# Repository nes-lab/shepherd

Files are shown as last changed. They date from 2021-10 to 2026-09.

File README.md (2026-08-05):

# SHEpHERD: SyncHronized Energy Harvesting Emulator RecorDer








**Testbed-Website**: <https://nes-lab.github.io/shepherd-nova>

**Python-Tools for Users**: <https://github.com/nes-lab/shepherd-tools>

**Documentation**: <https://nes-lab.github.io/shepherd>

**Main Project**: <https://github.com/nes-lab/shepherd>

**Targets-HW & -SW**: <https://github.com/nes-lab/shepherd-targets>

**WebAPI-Repo**: <https://github.com/nes-lab/shepherd-webapi>

**Dev-Documentation**: <https://github.com/orgua/shepherd-v2-planning>

---

Batteryless sensor nodes depend on harvesting energy from their environment.
Developing solutions involving groups of batteryless nodes requires a tool to analyze, understand and replicate spatio-temporal harvesting conditions.
*shepherd* is a testbed for the batteryless Internet of Things, allowing to record harvesting conditions at multiple points in space over time.
The recorded data can be replayed to attached wireless sensor nodes, examining their behavior under the constraints of spatio-temporal energy availability.

**Features**

 - High-speed, high resolution current and voltage sensing
 - Technology-agnostic: Currently, solar and kinetic energy harvesting are supported
 - Remote programming/debugging of ARM Cortex-M MCUs using Serial-Wire-Debug
 - High resolution, synchronized GPIO tracing
 - Configurable, constant voltage power supply for attached sensor nodes
 - Level-translated serial connection to the attached sensor nodes

For a detailed description see our [Paper](https://wwwpub.zih.tu-dresden.de/~mzimmerl/pubs/geissdoerfer19shepherd.pdf) or the [official documentation](https://nes-lab.github.io/shepherd/).

A *shepherd* instance consists of a group of spatially distributed *shepherd* nodes that are time-synchronized with each other.
Each *shepherd* node consists of a [BeagleBone](https://beagleboard.org/bone), the *shepherd* cape and either an energy harvesting source or a target MCU board to test.

This repository contains the hardware design files for the shepherd cape, the software running on each *shepherd* node as well as the tool to orchestrate a group of *shepherd* nodes connected to a network.

## Quickstart

Start by assembling your *shepherd* nodes, consisting of a BeagleBone Green/Black, a *shepherd* cape, a harvesting capelet and a target capelet.
The next step is to manually install the latest Ubuntu Linux on each BeagleBone.
You can install it to SD-card or the on-board eMMC flash, following [the official instructions](https://elinux.org/BeagleBoardUbuntu).
Make sure to follow the instructions for **BeagleBone**. Alternatively there are two more detailed guides in the [shepherd documentation](https://nes-lab.github.io/shepherd/user/getting_started.html).

The following instructions describe how to install the *shepherd* software on a group of *shepherd* nodes connected to an Ethernet network.
We assume that your local machine is connected to the same network, that the nodes have internet access and that you know the IP address of each node.

If you haven't done it yet, clone this repository to your local machine:

```shell
git clone https://github.com/nes-lab/shepherd.git
```

Next, install the tools used for installing and controlling the *shepherd* nodes.
We'll use [Ansible](https://www.ansible.com/) to remotely roll out the basic configuration to each *shepherd* node and *shepherd-herd* to orchestrate recording/emulation across all nodes.
The tools are hosted on `PyPI` and require Python version >= 3.6.
You'll also need to have `sshpass` installed on your machine, which is available through the package management system of all major distributions.
Install the tools using `pip`:

```shell
pip3 install ansible shepherd-herd
```

The `inventory/herd.yaml` file shows an example of how to provide the host names and known IP addresses of your BeagleBones.
Adjust it to reflect your setup.
You can arbitrarily choose and assign the hostnames (sheep0, sheep1, in this example) and the ansible_user (jane in this example).
[**TODO:** update description with roles].

```yaml
sheep:
  hosts:
    sheep0:
        ansible_host: 192.168.1.100
    sheep1:
        ansible_host: 192.168.1.101
    sheep2:
        ansible_host: 192.168.1.102
  vars:
    ansible_user: jane
```

Now run the `bootstrap.yml` *Ansible* playbook, which sets the hostname, creates a user and enables passwordless ssh and sudo:

```shell
ansible-playbook deploy/bootstrap.yml
```

Finally, use the `deploy.yml` playbook to set up the *shepherd* software with the configured roles from inventory:

```shell
ansible-playbook deploy/deploy.yml
```

## Usage

Record two minutes of data:

```shell
shepherd-herd harvester -d 120 -o recording.h5 -a mppt_voc
```
The command starts the recording asynchronously and returns after all nodes have started recording.
While the nodes are still recording (indicated by blinking of LED 1 and 2), prepare a directory on your local machine:

```shell
mkdir ~/shepherd_recordings
```

After the nodes stop blinking, you can retrieve the data to analyze it on your local machine:

```shell
shepherd-herd retrieve recording.h5 ~/shepherd_recordings
```

For a detailed description of the [HDF5](https://en.wikipedia.org/wiki/Hierarchical_Data_Format) based data format, refer to the [corresponding documentation](https://shepherd-testbed.readthedocs.io/en/latest/user/data_format.html).

Finally, replay the previously recorded data to the attached sensor nodes, recording their power consumption:

```shell
shepherd-herd emulator -o consumption.h5 recording.h5
```

Try `shepherd-herd --help` or check out the documentation [here](https://shepherd-testbed.readthedocs.io/en/latest/user/cli.html#shepherd-herd) for a list of all options.

## Problems and Questions

If you experience issues or require additional features, please get in touch via e-mail or by creating an issue on GitHub. The issue-tab also gives an overview for current roadmaps and milestones.

## People

*shepherd* development is lead at the Networked Embedded Systems Lab at TU Dresden & TU Darmstadt as part of the DFG-funded project Next-IoT.

The following people have contributed to *shepherd*:

 - [Kai Geissdoerfer](https://www.researchgate.net/profile/Kai_Geissdoerfer)
 - [Mikolaj Chwalisz](https://www.tkn.tu-berlin.de/team/chwalisz/)
 - [Marco Zimmerling](https://wwwpub.zih.tu-dresden.de/~mzimmerl/)
 - [Justus Paulick](https://github.com/kugelbit)
 - [Boris Blokland](https://github.com/borro0)
 - [Jonas Kubicki](https://github.com/jonkub)
 - [Ingmar Splitt](https://github.com/nes-lab)

## Release-Procedure

Once you have a clean, stable and tested version, you should bump the version number to current year, month and release-number (YYYY.MM.r).

- increase version number by executing ``bump2version`` (see cmds below)
- update changelog in ``CHANGELOG.md``
- run unittests locally
  - sheep-package on observers
  - herd-tool on host
  - pru-python-module (in `software/firmware/pru0-module-py`)
  - fresh installation on Linux image via ansible
  - additionally every push gets automatically tested by GitHub workflows
- install and run ``prek`` for QA-Checks (pre-commit plugin-replacement), see steps below
- move code from dev-branch to main by PR
- add tag to commit - reflecting current version number - i.e. ``v25.5.1``
  - GitHub automatically creates a release & pushes the release to PyPI
- update release-text with latest Changelog (from `CHANGELOG.md`)
- rebase dev-branch

```Shell
prek run --all-files

# additional QA-Tests (currently with open issues)
ty check

bump2version --allow-dirty --new-version 2026.08.1 patch
# version-format: YYYY.MM.r
```

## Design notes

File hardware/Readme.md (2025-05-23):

# Shepherd specific Hardware

## Overview

Hardware-Subdirectories contain the necessary design-files to manufacture a shepherd observer node.

- `_deprecated`: design files for hardware that still floats around in the lab
- `cape_v#.#`: most recent version of shepherd cape for the BBone
- `case_lasercut`: deployment version for testbed
- ~~`power_in`:~~ low noise voltage regulator with < 17 V Input for TP-Link POE-Adapters that fail to produce 5V on newer Cisco Switches
- Targets are in dedicated [targets-repo](https://github.com/nes-lab/shepherd-targets/tree/main/hardware)

## Photos

### Cape v2.4

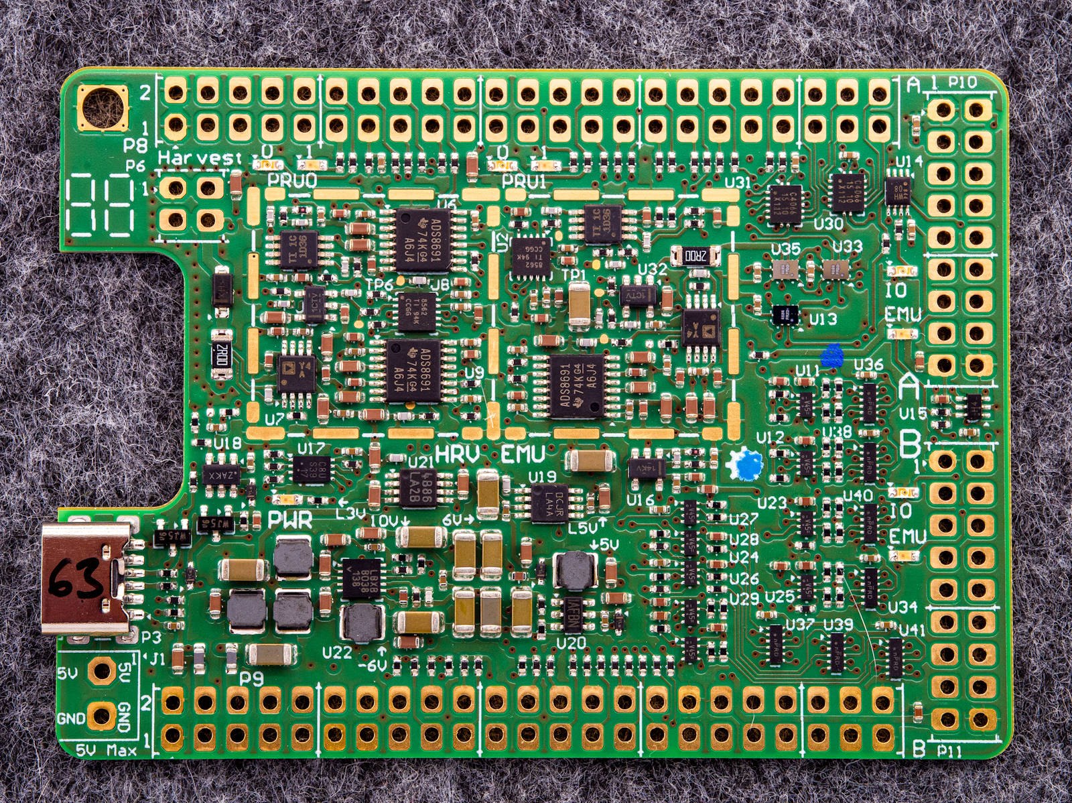
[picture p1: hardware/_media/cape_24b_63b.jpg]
Cape24b


More pictures are stored for QA in [planning-repo](https://github.com/orgua/shepherd-v2-planning/tree/main/doc_testbed/photos_PCBs).

### Cape v2.5

No pictures available yet. Hardware is currently tested and then deployed.

### Observers

Assembled in October 2024 for the deployment at TU Dresden. These nodes contain:

- TP-Link POE Splitter
- BeagleBone Green
- Shepherd Cape v2.4
- [nRF FRAM Target v1.3](https://github.com/nes-lab/shepherd-targets/tree/main/hardware/shepherd_nRF_FRAM_Target_v1.3e)
- Power-in-PCB
- Laser-cut case

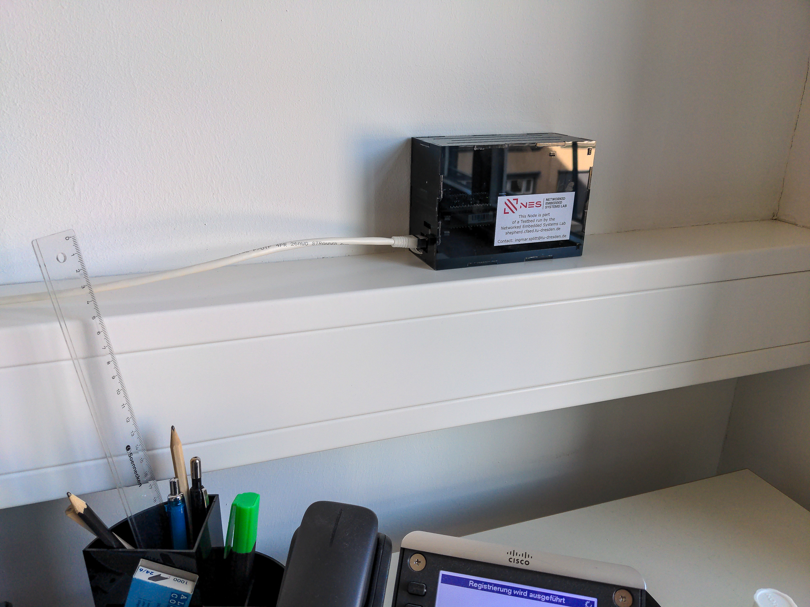
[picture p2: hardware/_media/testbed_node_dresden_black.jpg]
target_black


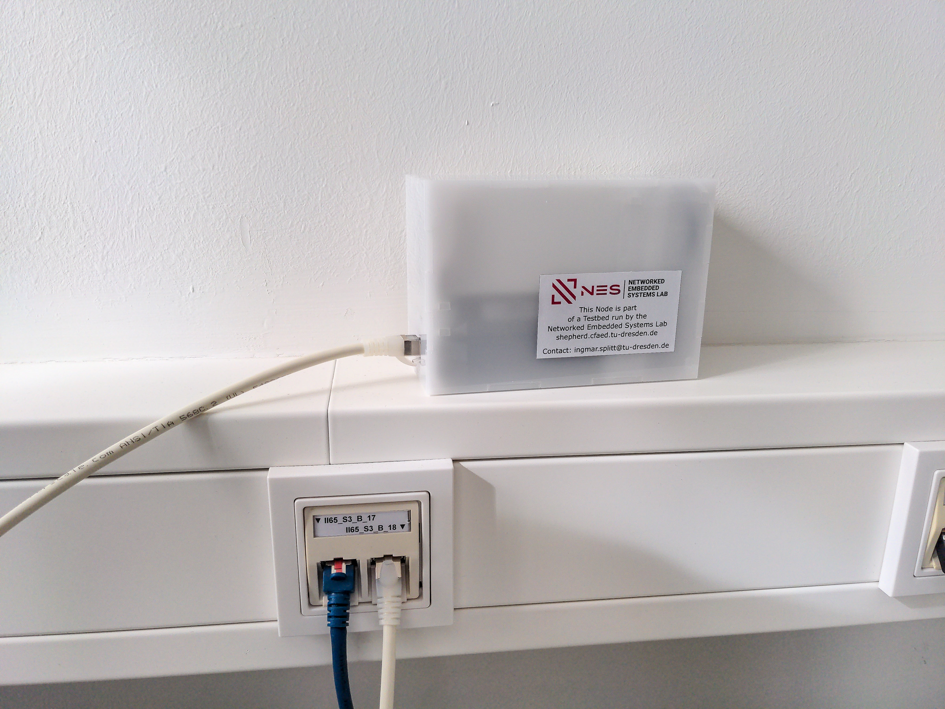
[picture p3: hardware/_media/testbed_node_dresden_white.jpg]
target_white


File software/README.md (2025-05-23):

# Software for Shepherd-Testbed

A collection of components and subprojects needed for the testbed. Bold items are needed for a local shepherd instance.

- **`firmware`**: time-critical gpio-sampling and emulation of virtual power source in PRUs of BeagleBone
- `gps-overlay`: kernel-module to allow syncing time via GPS
- **`kernel-module`**: low level system interface in between sheep-software (python) and PRUs
- `openocd`: (semi-deprecated) configuration for programming targets via openOCD
- `pps-gmtimer`: kernel-module to sync to a pps-time-signal
- **`python-package`**: sheep-software running on the beaglebone
- `shepherd-calibration`: python-software to calibrate the cape using a Keithley Sourcemeter
- `shepherd-tools`: sub-git for python user-module to handle measurements and access the data
- `shepherd-devicetest`: python-software to test & validate all parts of a cape
- **`shepherd-herd`**: python-software to control sheep / observers
- `shepherd-targets`: sub-git for target hardware and default firmwares
- `shepherd-webapi`: sub-git for the API and Website of the official testbed instance
- `debug_analyze_time_sync`: python-software for measuring sync between observers on gpio-level
- `debug_compare_vsources`: python-scripts to run virtual power source on PRU, shared-lib & python-port

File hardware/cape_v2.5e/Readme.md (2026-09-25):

## Main Goals

- replace old target connector by new edge connector
- redo interface to target completely
- add 17 V regulator to clean up POE-Supply
- add more GPIO (remove harvester as a tradeoff)

## Changes

### Implemented Changes v2.5a

- lower current-limiting resistors from 470 R to 240 R (see new target)
- emu U32 replace OPA189 by OPA388
- LP for InAmp AD8421 ⇾ 80kHz with 2x 100R, +2x 1nF to GND
- change invNr-Sys to solid white rect
- Emu - use 10mV Ref directly, without Switch
- Rec - use GND as Ref directly
- stabilize 10 mV ⇾ 1uF increase to 2x 10uF, 2R increase to 10R
- replace electrolytic Caps by MLCC (Optionals on Backside)

### Implemented Changes v2.5b/c

- production optimized for JLC
  - 6 layer includes via filling & capping (type 7) -> optional as via in pad is not used
  - vias were reduced to 0.2 mm hole, 0.35 ring dia
- replace target header with 40pin edge-Connector
- add 17V converter (previously external)
- Screw-Connector now supports 7 - 17V
- remove XYZ - for this last version - testbed only
  - usb-input
  - harvester frontend
  - ~~external switch & LED~~
- pin-changes on BBB Sockets, documented in `shepherd-git/hardware/_deprecated/beaglebone_pinout_concept.xlsx`
  - P8_14 is GPIO7, was targets GPIO0
  - P8_17 is GPIO8, was targets GPIO1
  - P8_27 is pru1_GPIO8, was pru_uart_tx
  - P8_28 is pru1_GPIO10, in addition to PRU1-LED0 (switch to input)
  - P8_29 is pru1_GPIO9, was pru1_batOK (switch to input)
  - P8_30 is pru1_GPIO11, in addition to PRU1-LED1 (switch to input)
  - P8_37 is now controlling direction of gpio-group A
  - P8_38 is now controlling direction of gpio-group B
  - P8_40 is pru1_GPIO7, was pru_uart_rx
  - P9_14 is now controlling direction of gpio-group C, was EN_Recorder
  - P9_25 is free, was CS_ADC2_REC
  - P9_27 is PWR_GOOD_L, was CS_DAC_REC
  - P9_41B is PWR_GOOD_H, was CS_ADC1_REC
- Target mapping Changed!
  - Target-GPIO9..11 are now input pru0-r31 (P8_29, P8_28, P8_30)
  - Target_GPIO0 is now UART-RX
  - BBone Pins changed
  - PinDirections are different
  - new BBone to target mapping is in separate section below, it now supports recording 12 pins
- GPS-Sync-Header added

### Implemented Changes v2.5d

- BOM-Trouble
  - NLAS4684 / NLAS4684FCT1G not available at all
    - Analog Switch, Dual SPDT, 500 mOhm Rds, 300 mA continuous, 500 mA peak, <10 nA Leakage (1 nA for -55 to 25°C)
    - we still have **~200x NLAS4684MN**, so will switch to that for now (+ larger, safer package)
  - PI5A4158 / PI5A4158ZAEX currently not avail
    - Analog Switch, Dual SPDT, 800 mOhm Rds, ~40 nA Leakage, high speed ~150 MHz with < 40 pF
    - PI3USB102G: 4 Ohm, 5V5 max, 6 pF, **BUT** 200 nA leakage
    - PI5A23157: 10 Ohm, 6V max, 18 pF, **BUT** 50 - 1000 nA leakage
    - **PI5A4157 / 729-PI5A4157CEX: single channel version of same IC, but only larger SC70 package (2.2x2.4) available**
    - **729-PI5A4157ZUEX**: UDFN-Package, 1x1 mm, mouser totally hides out of life parts, is in stock
  - LP2989-3.3 not avail as VSSOP-8 / TSOP
    - switch to WSON?
    - **926-LP2989AIMM33NOPB**, same but double the price
  - 10k 0402 667-ERJ-2GEJ103X -> 603-RC0402FR-7W10KL
  - 5.1k 0402 667-ERJ-2RKF5101X -> 603-RC0402FR-075K1L

## Implemented Changes v2.5e

- 1uF 10V is both used in 0402 & 0603
- holes on panel can be 3.2 mm for stencil printer
- QR Code can now be directly created in Altium
- larger tag-field (upper left corner)
- perforated breaking lines on panels  (extension of milled line)
- cage with paste?
- JST-Connector needs paste on mech-pad
- panel-bridge under JST - bad coincidence
- screw-hole could have vias around (safer, if inner metal scrapes off) -> it already has
- show label on 10mV
- add testpoints for voltages, avoid touching components
- Label reads "v2.5c" not 2.5d
- pin 1 marking bigger on most ICs
- **uart-sys pins are swapped, R66 & R68 need to be crossed manually**

## Errata & future Improvements

- ~~[modularize cape by function (Pwr, hrv, emu, gpio)](https://github.com/orgua/shepherd-v2-planning/blob/main/docs/10_capes/cape_v30_design.md)~~
  - reduce complexity
  - make iterations easier
  - reduce cost (cape is either hrv or emu)
  - trivial switching of platforms
- allow routing AUX-voltage (second output of DAC) to the same target port to mimic V_Sense to allow developing better intermittent algorithms (allows sensing emulated V_harvest or V_storage_cap)
  - two GPIO available for the analog switch (48, 117) - can be slow sysgpio
  - current 40 Pin target-connector has two NC pins left
- [route reset-line to target](https://github.com/nes-lab/shepherd/issues/164)
  - current 40 Pin target-connector has two NC pins left
- ~~support 4 Target Ports?~~
- Target-Connector is more useful right-angled, there are two versions:
  - `-RA`: SMD, right angle, Double the price
  - `-EM2`: Edge-mount, needs paste on both sides, even pricier than `-RA`
  - maybe it is cheaper to just plug in an interface PCB with a second connector to get the same result
- edge-PCB Target-Connector replace with FPC- or FCC-cable (flex-printed-circuit, flex-circuit-connector) to be less constraint positioning the target
  - features to keep: rotation-safe & shielded (currently 12x extra GND)
  - needed IO: 16 GPIO, 2 Voltages, 2 PwrGood, 4 Prog, 1+ GND => 25+ Pins
    - +1x for aux voltage
    - +1x for reset line (nRF & msp have nReset) -> 2 lines or negate if needed
    - +2x-3x for I2C-EEPROM (Write-Protection)
    - in total 5 pins extra
  - 40 pin FFC/FPC, 0.5 mm Pitch, 1.5€ -> 05-40-A-0050-A-4-06-4-T-HF
  - 40 pin connector has similar space req. as edge connector, 0.5 € per connector, FFC2B35-40-G
- NOTE: PI5 is the hardest part to place & source (but has to be replaced anyway)
  - main point of failure during production & hard to fix
- header to interface SBC as SMD? the goal is to speed up assembly with more automation
  - this would also make it worthwhile to p'n'p the bottom side (7 Caps)
- P2 Connector for external triggering & signaling has no real use-case
- describe P3 on PCB -> sync-port
- add shutdown-button (is missing on newer green eco)
- 5V input is enough - either add second input or remove 17V Reg (prone to burning out)

## Target Pin Def

### Target Port - Cape 2.4 (previous one)

```
pru_reg     name            BB_pin	sys_pin sys_reg
r31_00      TARGET_GPIO0    P8_45	P8_14, g0[26] -> 26
r31_01      TARGET_GPIO1    P8_46	P8_17, g0[27] -> 27
r31_02      TARGET_GPIO2    P8_43	P8_16, g1[14] -> 46
r31_03      TARGET_GPIO3    P8_44	P8_15, g1[15] -> 47
r31_04      TARGET_GPIO4    P8_41	P8_26, g1[29] -> 61
r31_05      TARGET_GPIO5    P8_42	P8_36, g2[16] -> 80
r31_06      TARGET_GPIO6    P8_39	P8_34, g2[17] -> 81
r31_07      TARGET_UART_RX  P8_40	P9_26, g0[14] -> 14
r31_08      TARGET_UART_TX  P8_27	P9_24, g0[15] -> 15
r30_09/out  TARGET_BAT_OK   P8_29	-
```

### Target Port - Cape 2.5d (this revision)

```
pru_reg       name              BB_pin	sys_pin sys_reg
pru1_r31_00   TARGET_GPIO0/uRx  P8_45	P9_26, g0[14] -> 14 (also Sys/PRU-UART) SYS_PINs have swapped UART
pru1_r31_01   TARGET_GPIO1/uTx  P8_46	P9_24, g0[15] -> 15 (also Sys/PRU-UART) SYS_PINs have swapped UART
pru1_r31_02   TARGET_GPIO2      P8_43	P8_16, g1[14] -> 46
pru1_r31_03   TARGET_GPIO3      P8_44	P8_15, g1[15] -> 47
pru1_r31_04   TARGET_GPIO4      P8_41	P8_26, g1[29] -> 61
pru1_r31_05   TARGET_GPIO5      P8_42	P8_36, g2[16] -> 80
pru1_r31_06   TARGET_GPIO6      P8_39	P8_34, g2[17] -> 81
pru1_r31_07   TARGET_GPIO7      P8_40	P8_14, g0[26] -> 26
pru1_r31_08   TARGET_GPIO8      P8_27	P8_17, g0[27] -> 27
pru1_r31_09   TARGET_GPIO9      P8_29	-
pru1_r31_10   TARGET_GPIO10     P8_28   - !! PRU1-LED0, direction must be changed in DTree for debugging
pru1_r31_11   TARGET_GPIO11     P8_30   - !! PRU1-LED1, direction must be changed in DTree

pru0_r30_05   PWR_GOOD_L        P9_27     (was CS_DAC_REC), gets added to bit 12 for GPIO-Sampling
pru0_r30_06   PWR_GOOD_H        P9_41B    (was CS_ADC1_REC), gets added to bit 13 for GPIO-Sampling
pru0_r30_07   - (free)          P9_25     (was CS_ADC2_REC)
```

## Commissioning Steps & Tests

### Manual Soldering

- 2Pin Screw-Header ⇾ VoltageInput
- 2x 2x46 Pinheader ⇾ BBone Port
- 5x 220 uF 6V3 MLCC on backside
- 2x 47 uF 16V MLCC 0on backside

### Initial Test

- visual
  - all ICs and diodes correct orientation
  - no visible shorts or other defects
  - R13 is DNP (at left edge, middle, next to coil)
- 7V In:
  - 15-17 mA, with 18x PI5 180deg flipped
  - 14-15 mA with PI5 removed or correctly oriented
  - first converter (U5/TPS62913) and its coil warms up by 7 K above ambient
- EN-Pin: 52-55 mA, OK, Converter +10K
  - 5V In directly after 17V stage (with TPS removed) 1 mA off vs 50 mA when on
  - warmest part is U3 - AD8421 InAmp (+5K from Ambient)
  - Power-Hotspots: U22, U19, U21,
  - Emu-Hotspots: U4, U3, U1,
  - GPIO-Hotspots: U7 (only one of many?)
- Voltages
    - L5V ⇾ 5.000 V
    - L3V3 ⇾ 3.295 V
    - 6V ⇾ 6.19 V
    - 10V ⇾ 9.71 V
    - -6V ⇾ -5.99 V
    - 10mV ⇾ 0.010 V
    - 5V ⇾ 5.20 V

### Verification and Log

Logs are stored in [Planning-Repo](https://github.com/orgua/shepherd-v2-planning/blob/main/doc_testbed/Cape25e_pre-deployment-tests.xlsx)

run test-firmware with real harvest (will be intermittent)

```Shell
sudo shepherd-sheep -v run ./python-package/example_config_emulation.yaml
```

run test-firmware with direct-vsrc and 3000mV recording

```Shell
sudo shepherd-sheep -v run /etc/shepherd/example_config_emulation.yaml
ll /var/shepherd/recordings/
scp jane@sheep0://var/shepherd/recordings/emu_2026-02-* ./
# -> run also on second port
```

Plot both

```Shell
shepherd-data plot .\ -e10
shepherd-data plot .\ -e"0.2"
```

Extract GPIO

```Shell
shepherd-data extract-gpio .\
# ! GPIO9to11 show no movement, these are allwaysRX, same as GPIO8 -> old device-tree
```

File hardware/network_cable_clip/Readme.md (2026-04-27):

# 3D-Printed Cable Clip

## Features

- holds cable with up to 6.5 mm diameter cable
- can take 1 to 4 magnets (4 mm diameter, 2 mm height)
- magnets can be pushed inside from the side of the cable-channel
- < 1 g PLA filament
- can be printed without support

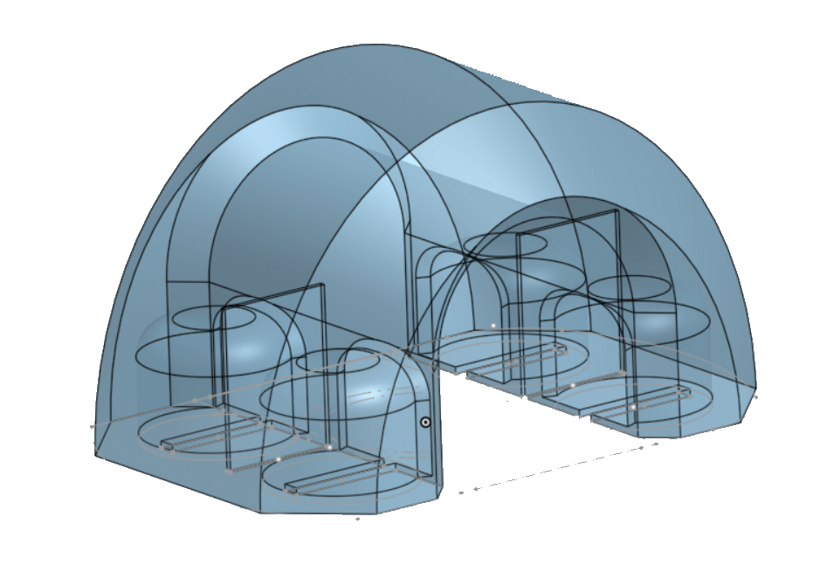
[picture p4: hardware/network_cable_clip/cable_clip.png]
rendered


[Designed in onshape](https://cad.onshape.com/documents/66bf84de817494616f210bb4/w/bc75bb6701e47c344748dd48/e/8d123086b6a33f87c60c09e2)

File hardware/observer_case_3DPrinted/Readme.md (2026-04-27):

# 3D Printed Case for the Observer Nodes

## Features

- high airflow case for Beaglebone, Cape & POE-Adapter
- internal rails for the PCBs
- feet with space for cylindrical magnets (8x3 mm, Dxh) for over head installation
- two parts that clip together
- openings for all emulator related ports
- 36 g PLA filament
- can be printed without support (flip end-face to print-plate)

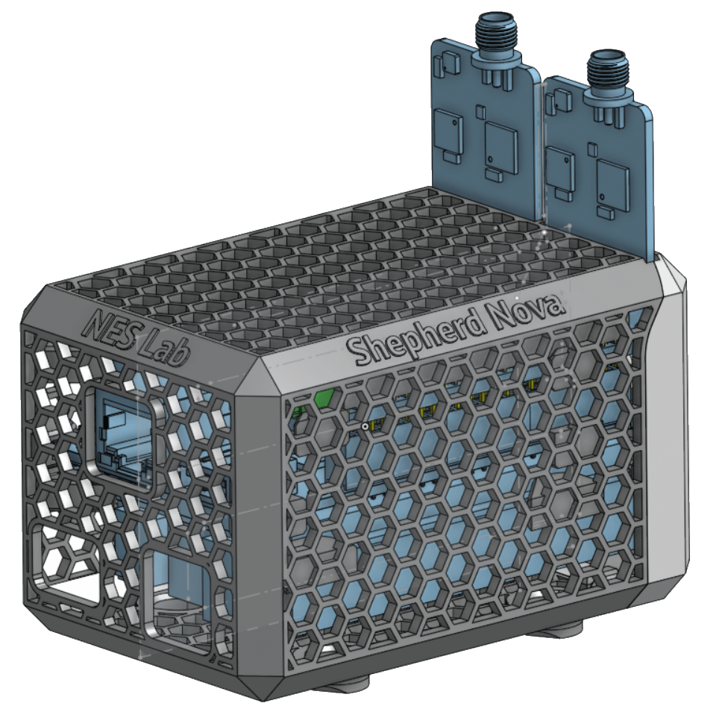
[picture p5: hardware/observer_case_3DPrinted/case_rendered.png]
rendered


[Designed in onshape](https://cad.onshape.com/documents/cdcbe7f9671a626c8653eaf6/w/935ef12e9d106129efaf4b0b/e/58438ca06a4c5f672a67230e)

## Pending Improvements

- need for more or longer initial rails
- better BBB rail - the stack slides out easily - so also cover the solder joints of the header
- power cable in front should have more space or dedicated hole
- case could be smaller: back 1 mm, top 1 mm, sides 1 mm
- make rail-parts go half way or fully into mesh
- refactor, as the project got messy at the end

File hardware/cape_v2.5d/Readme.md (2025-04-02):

## Main Goals

- replace old target connector by new edge connector
- redo interface to target completely
- add 17 V regulator to clean up POE-Supply
- add more GPIO (remove harvester as a tradeoff)

## Changes

### Implemented Changes v2.5d (compared to 2.5c)

- BOM-Trouble
  - NLAS4684 / NLAS4684FCT1G not available at all
    - Analog Switch, Dual SPDT, 500 mOhm Rds, 300 mA continuous, 500 mA peak, <10 nA Leakage (1 nA for -55 to 25°C)
    - we still have **~200x NLAS4684MN**, so will switch to that for now (+ larger, safer package)
  - PI5A4158 / PI5A4158ZAEX currently not avail
    - Analog Switch, Dual SPDT, 800 mOhm Rds, ~40 nA Leakage, high speed ~150 MHz with < 40 pF
    - PI3USB102G: 4 Ohm, 5V5 max, 6 pF, **BUT** 200 nA leakage
    - PI5A23157: 10 Ohm, 6V max, 18 pF, **BUT** 50 - 1000 nA leakage
    - **PI5A4157 / 729-PI5A4157CEX: single channel version of same IC, but only larger SC70 package (2.2x2.4) available**
    - **729-PI5A4157ZUEX**: UDFN-Package, 1x1 mm, mouser totally hides out of life parts, is in stock
  - LP2989-3.3 not avail as VSSOP-8 / TSOP
    - switch to WSON?
    - **926-LP2989AIMM33NOPB**, same but double the price
  - 10k 0402 667-ERJ-2GEJ103X -> 603-RC0402FR-7W10KL
  - 5.1k 0402 667-ERJ-2RKF5101X -> 603-RC0402FR-075K1L

## Errata & future Improvements

- 1uF 10V is both used in 0402 & 0603
- holes on panel can be 3.2 mm for stencil printer
- QR Code can now be directly created in Altium
- larger tag-field (upper left corner)
- perforated breaking lines on panels  (extension of milled line)
- cage with paste?
- JST-Connector needs paste on mech-pad
- panel-bridge under JST - bad coincidence
- screw-hole could have vias around (safer, if inner metal scrapes off) -> it already has
- show label on 10mV
- add testpoints for voltages, avoid touching components
- Label reads "v2.5c" not 2.5d
- pin 1 marking bigger on most ICs
- **uart-sys pins are swapped, R66 & R68 need to be crossed manually**

Up to here implemented in v2.5e

- header to interface SBC as SMD?
- NOTE: PI5 is the hardest part to place & source (but has to be replaced anyway)

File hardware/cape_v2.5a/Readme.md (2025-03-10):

## Implemented Changes v2.5a

- lower current-limiting resistors from 470 R to 240 R (see new target)
- emu U32 replace OPA189 by OPA388
- LP for InAmp AD8421 ⇾ 80kHz with 2x 100R, +2x 1nF to GND
- change invNr-Sys to solid white rect
- Emu - use 10mV Ref directly, without Switch
- Rec - use GND as Ref directly
- stabilize 10 mV ⇾ 1uF increase to 2x 10uF, 2R increase to 10R
- replace electrolytic Caps by MLCC (Optionals on Backside)

## Changes and Errors for future Version

- replace target header with 40pin edge-Connector
- keep pin-mapping of target v1.0
- add more dir-changing (reuse 2x Dir of prog-adapter)
- harvester seems a bit too fast - current is overswinging - see SM141K04LV ivcurve
- disable GPIO IO if voltage is cut (due to low_threshold)
- second bat-ok

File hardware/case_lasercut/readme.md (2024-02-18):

# LaserCut Case-Concept

## Inner Parts

- POE-Splitter 82x54x25
- BB + Cape 90x55x27
- Target Z+35
- NW-Plug X+40
- Rail Z+3
- NOTE: BB+Target are Z=56mm but above values have 6mm buffer

Inner-Dimensions

- X = 90 + 40 = 130
- Y = 55
- Z = 25 + 27 + 35 + 3 = 90

3mm Material - Outer Dimensions

136 x 61 x 96

Area: 532 cm²

## External Features

- Opening for
  - NW-Plug (15x13)
  - sd-card (15x4)
- Convection-Slots
- pluggable inner structure to hold parts in place
  - 2x POE-Splitter
  - 2x BBone
- magnet-holder to fix
    - var1: 15x3mm round, with 3.5mm hole, n45 -> screw-able
    - var2: 20x10x1, N42, with adhesive, ~1.8kg
    - var3: 10x5x1, N45, Adhesive, 700g,

## Coordinates

### Bottom

V-Stab
- X = 136 - 82 - 3 - 3 -5 = +43
- Y1 = +3
- Y2 = +55

### Bottom & Top

Vents
- X1 = 13
- X2 = 23
- Y1 = 29 - 14 = 15
- Y2 = 61/2 - 3/2 = 29
- Y3 = 29 + 14 = 43

### Sides

H-Rail
- X = 136 - 3 - 3 - 5= + 125
- Z1 = 96 - 3 - 25 - 3 = -65 (from top)
- Z2 = 96 - 3 - 25 - 3 - 3 -9 = -53

H-Arret:
- X = 136 - 3 - 82 - 14 = +37
- Z = 3 + 5 = -8 (from top)

H-Front:
- X = 3 + 1 = +4
- Z1 = 3+ 3 = -6 (from top)
- Z2 = 96 - 3- 3 -5 = -85

### Back

NW
- Y = 3 + 15 = 18
- Z = 3 + 6 = 9

SD
- Y = 3 + 10 = 13
- Z = 3+ 25 +2 = 30

### Box-Fingers

- X130/5: 26, 52, 78, 104
- Y55/3: 18, 37
- Z90/5: 18, 36, 54, 72

## BOX-Generators

https://github.com/paulh-rnd/TabbedBoxMaker
https://www.makercase.com/#/basicbox
https://boxdesigner.connectionlab.org/
https://makeabox.io/
https://jeromeleary.com/laser/  -> Fav, but finger-sections are off ?!?

## Manufacturing

https://www.formulor.de/
    -> matt, opak, mineral gray, 9643
    -> matt, opak, moonlight white, S2 1T41
    -> schwarz, opak, einseitig, matt, 9H01 SC
    -> mittelgrau, transparent 7C83 -> Fav
    -> weiß, milchig, WH02 -> Fav
https://www.plexilaser.de/shop/Acrylglas-transparent-Eisblau
https://www.plexilaser.de/shop/Acrylglas-satiniert-Duo-Night-Day -> Fav
https://www.plexilaser.de/shop/Acrylglas-satiniert-Milchglasoptik -> Fav

## Assembling

- parts are glued together with PMMA-compatible glue
- leave outer protective layer on while gluing
- parts can be put together all at once and fixed rubber-bands

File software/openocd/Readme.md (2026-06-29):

# OpenOCD Programming

## Pin Definition

This method was already used on shepherd v1, but now there is a level-shifter with discrete direction-pin between SBC and Target.
The relevant GPIO for programming are printed below.

### Prog 1

CLK - P9_17 - GPIO[5]
DIO - P9_18 - GPIO[4]
DIR - P8_31 - GPIO[10]
DevTree configures these pins already as GPIO!

### Prog 2

CLK - P8_35 - GPIO[8]
DIO - P8_33 - GPIO[9]
DIR - P8_32 - GPIO[11]
DevTree configures these pins already as GPIO!

## Preparation

First install OpenOCD

```shell
sudo apt install openocd
```

Activate Port A or B with

```Shell
sudo shepherd-sheep -v target-power --gpio-pass --target-port=A
#sudo shepherd-sheep -v target-power --gpio-pass --target-port=B
```

## HowTo

### Info

```Shell
sudo openocd -f shepherd.cfg -c init -c targets -c 'nrf5 info' -c exit
```

## Erase

Mass-erase

```Shell
sudo openocd -f shepherd.cfg -c init -c 'reset halt' -c 'nrf5 mass_erase' -c exit
```

Chip-Erase

```Shell
sudo openocd -f shepherd.cfg -c init -c 'reset halt' -c 'nrf52_recover' -c exit
sudo /usr/bin/openocd -f /opt/shepherd/software/openocd/shepherd.cfg -c 'init; reset halt; nrf52_recover; exit;'
```

### Program

```Shell
sudo openocd -f shepherd.cfg -c "program /opt/shepherd/hardware/tests_manual/nrf52_testable.hex verify reset; exit;"
```

Works, with the output

```Shell
Open On-Chip Debugger 0.12.0
Licensed under GNU GPL v2
For bug reports, read
        http://openocd.org/doc/doxygen/bugs.html
adapter speed: 10 kHz

Info : Linux GPIOD JTAG/SWD bitbang driver
Info : This adapter doesn't support configurable speed
Info : SWD DPIDR 0x2ba01477
Info : [nrf52.cpu] Cortex-M4 r0p1 processor detected
Info : [nrf52.cpu] target has 6 breakpoints, 4 watchpoints
Info : starting gdb server for nrf52.cpu on 3333
Info : Listening on port 3333 for gdb connections
[nrf52.cpu] halted due to debug-request, current mode: Thread
xPSR: 0x01000000 pc: 0x00000134 msp: 0x20002000
** Programming Started **
Info : nRF52840-xxAA(build code: D0) 1024kB Flash, 256kB RAM
Warn : Adding extra erase range, 0x0000307c .. 0x00003fff
** Programming Finished **
** Verify Started **
** Verified OK **
** Resetting Target **
shutdown command invoked
```

## Shortcuts

The config was extended for useful functions:

```Shell
sudo openocd -f shepherd.cfg -c chip_erase
sudo openocd -f shepherd.cfg -c mass_erase
sudo openocd -f /opt/shepherd/software/openocd/shepherd.cfg -c 'prog /opt/shepherd/hardware/tests_manual/nrf52_testable.hex'
# now integrated into sheep
sudo shepherd-sheep program -pA -m1 --mcu-type nrf52 /opt/shepherd/hardware/tests_manual/nrf52_testable.hex
```

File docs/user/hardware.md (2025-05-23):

# Hardware

## Overview

Shepherd is a HW/SW solution and this section describes the key interfaces of the shepherd hardware that are relevant to users.

Each shepherd observer consists of four key components:

- The BeagleBone is a Single Board Computer, handling synchronization, data storage and hardware control
- The shepherd cape contains the harvester- and emulator-circuitry and all other fixed hardware parts
- an optional harvesting adapter can be used to interface a harvesting transducer (e.g. solar panel) to the harvesting-port on the cape
- The target pcb connects a sensor node (e.g. a microcontroller with radio) to the emulator-circuit

## The Cape

This custom PCB contains the analog frontend for harvesting & emulation operations.
The included components and features are:

- the emulator and harvester consist of a purpose-fully chosen combination of low-noise and high-speed DACs, ADCs and Instrumentation-Amplifiers

  - both circuits can handle 0 - 5 V with up to 50 mA current
  - LSB is ~ 200 nA and ~ 20 uV for voltage- and current-measurements

- two target-ports for the emulator, user choice
- two parallel power rails available for the targets (one with current measurement, switchable)
- one default target with a nrf52-module (see below)
- 9 GPIO-Channels between target and system (fully monitored), switchable direction on some channels
- 4 programming-lines to each target for JTAG, SWD or SBW
- level translated gpio is designed to prevent the transfer of energy. it is also possible to completely disconnect the target
- watchdog to recover from hangups during unsupervised operation
- screw-in power-socket or type-c connector
- eeprom to store calibration and cape-config

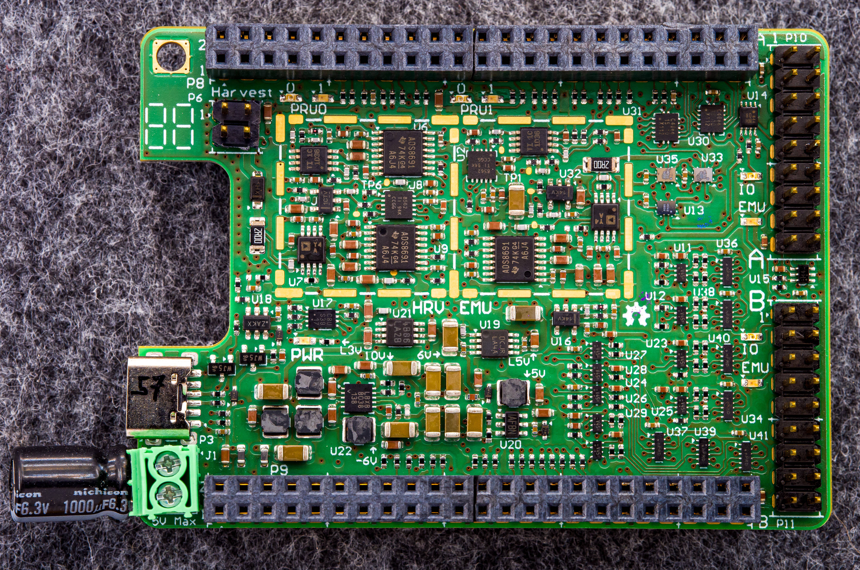
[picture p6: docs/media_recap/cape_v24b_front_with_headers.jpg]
cape_soldered


### References

- [/hardware-directory](https://github.com/nes-lab/shepherd/tree/main/hardware): contains cape, housing and additional design-files

## Harvesting Port

The harvesting port connects to any type of harvester, e.g., a solar panel or piezo-electric element to the shepherd hardware.
Some transducers need some external circuitry to work properly or for protection.
By keeping this part of the hardware separate from the main shepherd cape, we allow to easily connect various types of harvesters, without having to change the complex and expensive main cape.

:::{table} Header P6 pinout

| Pin | Description                                |
|-----|--------------------------------------------|
| 1   | Ground                                     |
| 2   | Voltage sensing input of harvest-circuitry |
| 3   | (optional) custom voltage from spare DAC   |
| 4   | Current sinking input of harvest-circuitry |
:::

## Harvesting Sources

Examples of tested and deployed energy harvesting sources.

### Solar

- Name: Anysolar - IXOLAR - SM141K06L
- Source: Light
- Operation: 4.15 VDC open, 184 mW Max, 3.35 V Pmpp, 58.6 mA Short
- Price: 4.80 € 1x, 3.47 € 100x
- Link: <https://www.digikey.de/product-detail/de/anysolar-ltd/SM141K06L/SM141K06L-ND/9990462>

### Piezo

- Name: Mide - S128-J1FR-1808YB
- Source: Mechanical Vibration
- Operation: 23.2 VDC, 16 mW
- Price: 64,77 € per Module
- Link: <https://www.mouser.de/ProductDetail/Mide/S128-J1FR-1808YB?qs=%2Fha2pyFadugcWv6TUOmJo5PvQenH8AtGZXSLNQdw9t1p66yQjFtz4w==>

This specific transducer needs an adapter with

- full bridge rectifier for the transducer (with low voltage drop)
- resistive voltage divider for max 5V v_sense (MOhm-Range)

## Target Port

Shepherd provides two identical generic interface-ports to connect any type of cyber-physical system. These can be supplied by emulated energy traces, while tracing its state via GPIO and UART output.

The target pcb connects to the shepherd cape via the dedicated headers P10 & P11 on the right side of the board.

:::{table} Header P10 / P11 pinout

| Pin | Description (Rx/TX always with reference to Observer)              |
|-----|--------------------------------------------------------------------|
| 1   | Ground                                                             |
| 2   | Emulator-Output V_Target                                           |
| 3   | GPIO0, RX & TX (Group1)                                            |
| 4   | GPIO1, RX & TX (Group1)                                            |
| 5   | GPIO2, RX & TX (Group1)                                            |
| 6   | GPIO3, RX & TX (Group1)                                            |
| 7   | GPIO4, always RX                                                   |
| 8   | GPIO5, always RX                                                   |
| 9   | GPIO6, always RX                                                   |
| 10  | GPIO7, always RX, also UART-RX to BBone UART1                      |
| 11  | GPIO8, RX & TX (Group2), also UART-TX to BBone UART1               |
| 12  | BAT OK, always TX, generated by PRU on BBone                       |
| 13  | Program1-CLK - Clock for remote programming (SWD, SBW) or JTAG-TCK |
| 14  | Program1-IO - Data for remote programming (SWD, SBW) or JTAG-TDI   |
| 15  | Program2-CLK - Clock for remote programming (SWD, SBW) or JTAG-TDO |
| 16  | Program2-IO - Data for remote programming (SWD, SBW) or JTAG-TMS   |
| 17  | +3V3, use for any additional infrastructure circuitry              |
| 18  | Ground                                                             |
:::

Notes:

- GPIO is always voltage translated and the direction is switchable in groups when noted in table.
- Pin 17 provides regulated 3.3V to supply any additional circuitry independent of the energy-tracing. This could be used to power, for example, a mosfet controlled debugging LED.
- Pins 10 and 11 expose the level-translated signals to UART1 on BeagleBone. They can be used to trace UART messages from the target sensor node.
- Pins 3 to 11 are (level-translated) connected to the low-latency GPIOs that are sampled by shepherd software for GPIO tracing.
- Pin 12 is tied to the virtual power source model and signals a power-good.
- Pins 13 to 16 (level-translated) are used to program/debug a connected sensor node with SWD, SBW or JTAG. This enables support for a wide range of microcontrollers.
- The header is symmetrical and therefore basically safe to reverse - so errors should not result in broken hardware.

## nRF-Target

This is shepherds current main target, hosting a nRF52 and MSP430, similar to the [Riotee](https://www.riotee.nessie-circuits.de) platform. Unfortunately the Riotee-SDK is not completely compatible for now, as the target is missing the hysteresis-function for the power-good-signal, which requires two pins.

The components and features are:

- MCU1: nRF52840
- MCU2: MSP430FR5962, 16 MHz, 128 kB FRAM, 8 kB SRAM, 68 IO, 12 bit DAC
- shared GPIO, Chip2Chip / SPI, LEDs, I2C RTC
- over-voltage protection for V_LV (max 3.9V)
- two debug LEDs with separate supply
- one self-powered LED to "burn" energy
- io pins not interfering with RF (nRF PS v1.6 page 578)
- LEDs / UART similar to Riotee
- LEDs have minimal impact on pwr-budget
- nRF uses low voltage mode (PSv1.1 page 61)
- 3rd possible way for reset (external), beside JTAG and pwr-cycle

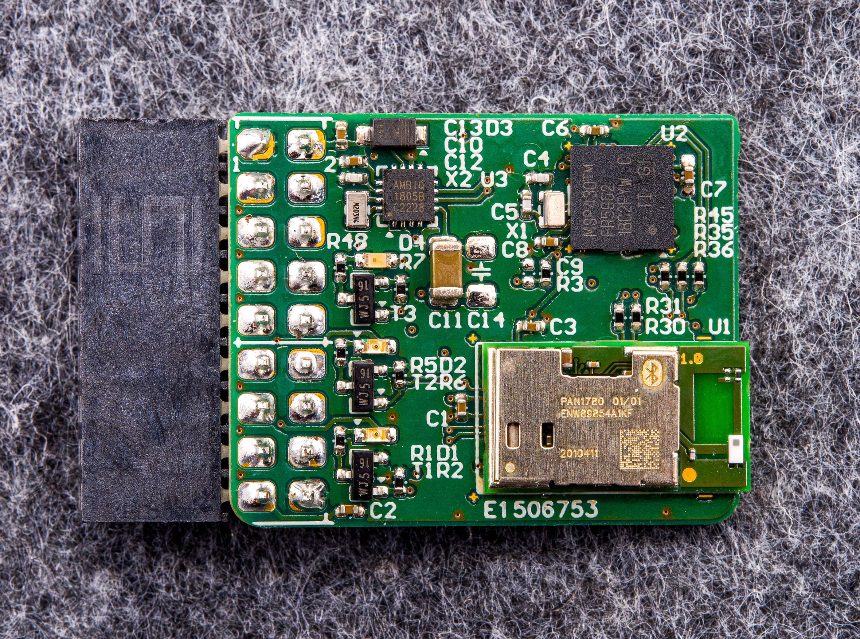
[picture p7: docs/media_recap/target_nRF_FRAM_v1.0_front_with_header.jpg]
target_soldered


### References

- [shepherd-targets-repo](https://github.com/nes-lab/shepherd-targets): contains hardware and software sources for supported targets

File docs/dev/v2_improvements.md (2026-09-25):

# Improvements of Shepherd v2

## Overview

### About Shepherd v1.x (from git)

Shepherd is a testbed for the batteryless Internet of Things, allowing to record harvesting conditions at multiple points in space over time. The recorded data can be replayed to attached wireless sensor nodes, examining their behavior under the constraints of spatio-temporal energy availability.

### About Shepherd v2.x

Previous description is still correct, in detail:

- embedded linux board with analog frontend serves as a shepherd node
- harvesting-circuit can record an energy trace from an energy-source like solar, thermoelectric, …
- emulation-circuit replays the energy-trace for a real target (user programmable uController) and records the drawn energy

**Version 1** is build around a BQ25504-IC (plus capacitor) as harvester for recording and emulating various environments. This is a valid approach, but limited by design:

- BQ-MPPT-controller is slow to react on changing environmental conditions by design (check every 16s with 64 ms downtime)
- (VOC-)mppt-controller is fairly simple with pre-set setpoint (e.g. 76 % of open-circuit voltage for solar cells)
- recorded harvest-environment is specific to harvest-IC + configuration
- setup / configuration (especially) with storage cap is fairly static (combination of MPPT-Controller, Boost-Converter, Cap)

**Version 2** improves the project by generalizing the basic idea and therefore virtualizing the harvester, storage capacitors and voltage converters. By switching to a software defined / virtual harvester-system and power-source the disadvantages from v1 vanish, with further advantages.

### Virtual Source

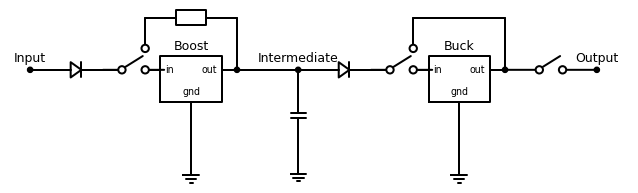
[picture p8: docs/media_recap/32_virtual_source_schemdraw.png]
schematic_vsource


- full customization per config-parameters (e.g. boost-voltage, capacitor size, …)

  - currently 10 parameters for the harvester, and
  - 29 parameters for the converter-stage

- harvesting-recorder has already several strategies implemented

  - constant voltage (CV)
  - MPPT, based on open circuit voltage or perturb & observe

- harvesting can be postponed by sampling

  - iv-curves from the energy-source
  - model-parameters like voc and isc for solar (higher rate than iv-curves)

- emulation handles harvested energy-traces or harvests directly from the iv-curves and simulates a customizable converter-stage
- power-stage has already predefined templates for several setups

  - direct throughput of traces
  - diode + capacitor (converterless)
  - buck-boost-converter (e.g. BQ25570) including the power-good-signal and efficiencies of underlying converters
  - buck-converter (BQ25504)

- the design enables users to automate testing of harvesting-setups e.g. by sweeping through parameters like storage-cap-size
- the emulator and harvester consist of a purpose-fully chosen combination of low-noise and high-speed DACs, ADCs and Instrumentation-Amplifiers

  - both circuits can handle 0 - 4.2 V (hrv even 5.0V) with up to 50 mA current
  - resulting resolution 18 bit, step size is ~ 200 nA and 20 uV for voltage and current

- the software-implementation updates in real time with 100 kHz

### General improvements for shepherd

- synchronization of sampling-trigger for node network optimized from ~ 2.4 us to under 500 ns
- jitter of sampling trigger improved from about +- 600 ns to under 100 ns
- two target-ports available, selectable via setup-parameter
- two parallel power rails available for the targets (one with current measurement, switchable)
- one default target with a nrf52-module
- 9 GPIO-Channels between target and system (pru-monitored)

  - partly bidirectional, switchable
  - relatively stable 4.03 MHz, min: 602 kHz, max: 4.55 MHz
  - previously ~ 160 - 1500 kHz, with 6 GPIO

- watchdog to handle hangups during unsupervised operation (and wakeups for saving power)
- screw-in power-socket or type-c connector

### Currently under development

- software programmer (in pru) for SWD & SpyBiWire
- advanced target with msp430 (with FRAM) and nrf52 for various configurations: only 1 uC active, msp as processor and nrf as radio, nrf as processor+radio and msp as low-energie storage
- combined network of shepherd nodes as iot-testbed with web-based control
- update doc
- advanced PRU-Firmware without virtual harvester & source, but higher min rate for gpio-sampling (goal: > 5 MHz)
- GPIO-Actuation

### Bigger challenges in near future

- hardware is getting quite old, but luckily software is improving (getting faster)
- ~~kernel 4.19 currently works (but has flaws) -> latest updates to 5.10 break kernel-module & pru
- chip-shortage is limiting our supply - 2 ICs only 15 left, current restock date mid '23

## Features in Detail

- disclaimer: graphs and stats are partly outdated
- scraped from the planning-git

### Hardware

in [](../user/hardware)

#### Shepherd Cape v2.4

- chip shortage forced us to a ultra fine pitch (350 um) -  risky and hard to hand-solder
- 360 components, 55 unique - > tedious, but ok to hand-solder
- switch to 6 layer due to higher gpio-count
- 1 Free Pin left on BBone

shpcape24b

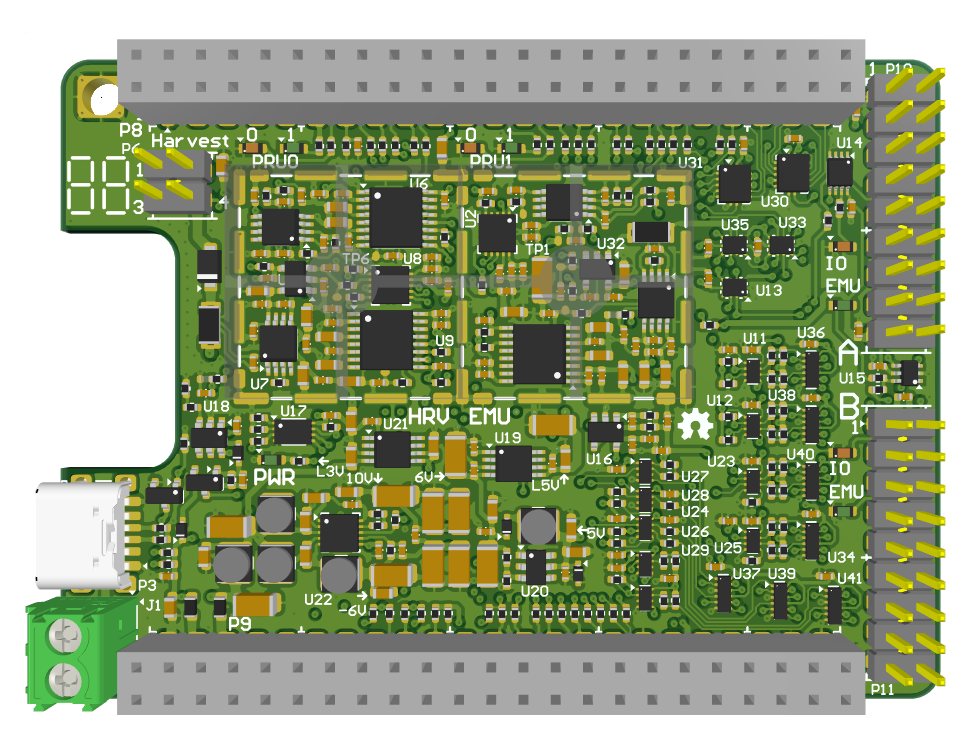
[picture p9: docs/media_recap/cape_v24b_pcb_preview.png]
shpcape24


#### nRF52 FRAM Target v1.0

- Target with MSP430 (FRAM) & nRF52 on one PCB

nrf52msp430target1

### Harvester Circuit

#### Schematic

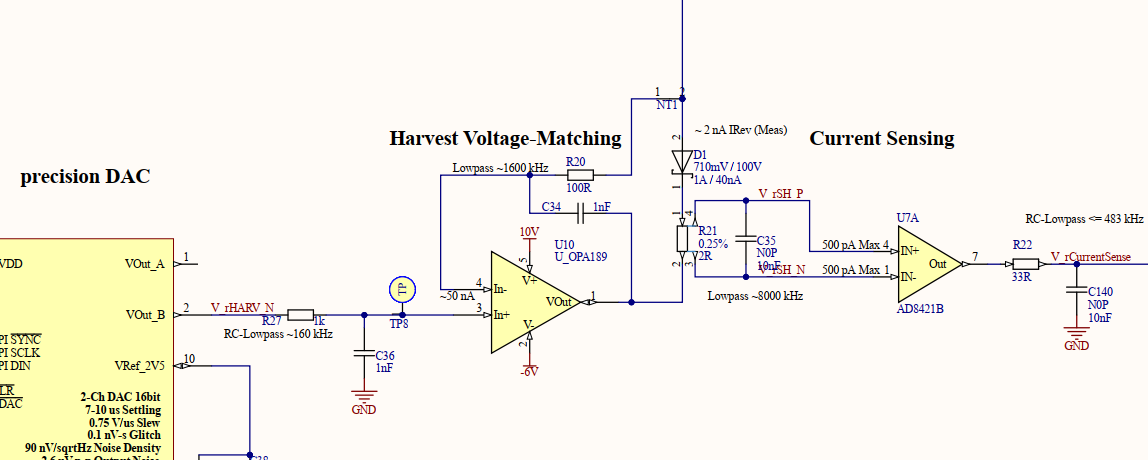
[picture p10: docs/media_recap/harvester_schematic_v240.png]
schematic_hrv


#### Diode selection

- datasheets only promise < 40 nA

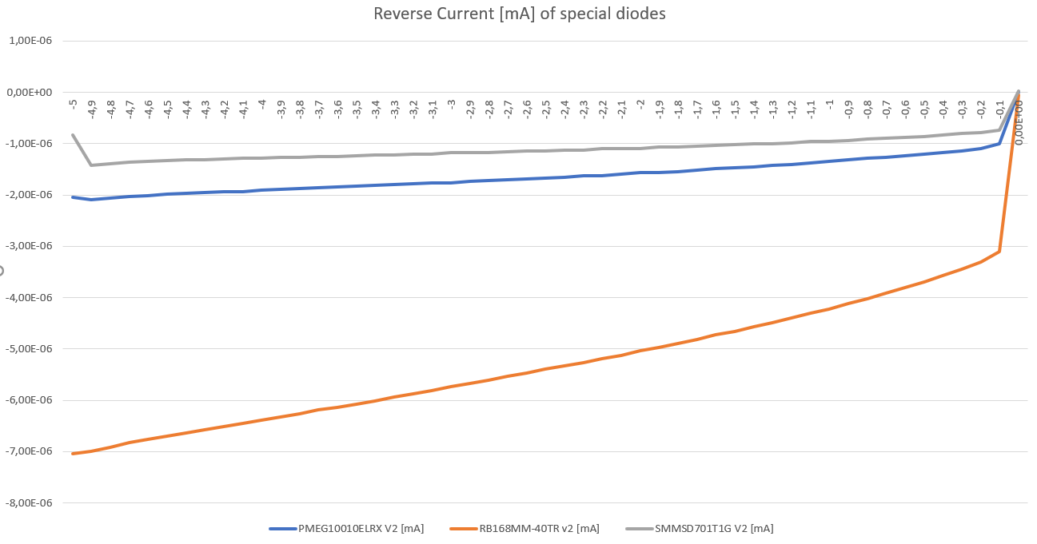
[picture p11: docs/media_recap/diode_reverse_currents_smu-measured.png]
hrv_diodes


#### Fine tuning Filters

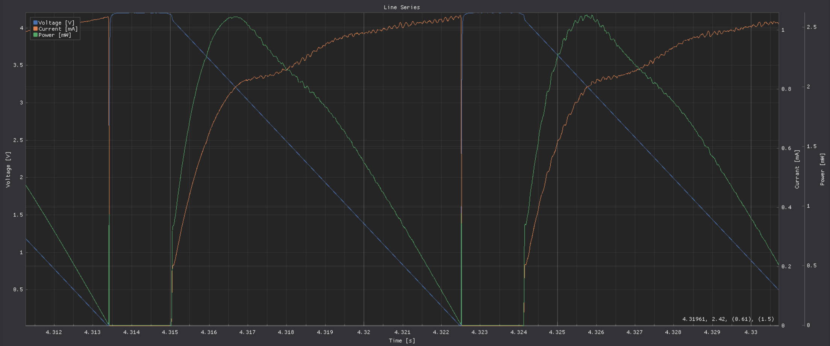
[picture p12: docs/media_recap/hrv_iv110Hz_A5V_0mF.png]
hrv_untuned


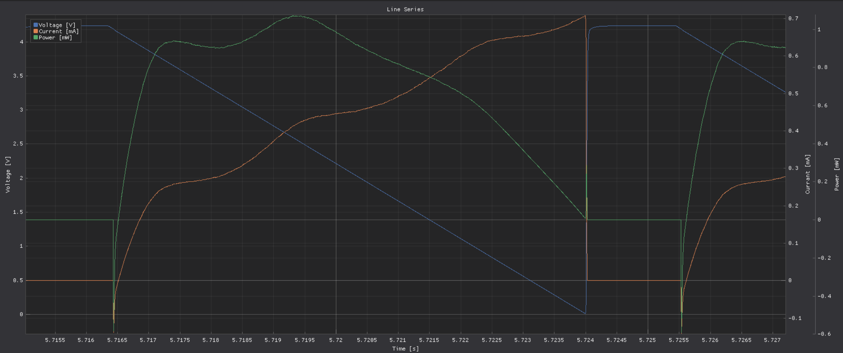
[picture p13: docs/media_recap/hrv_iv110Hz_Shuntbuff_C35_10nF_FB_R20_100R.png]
hrv_tuned


#### Resulting Performance

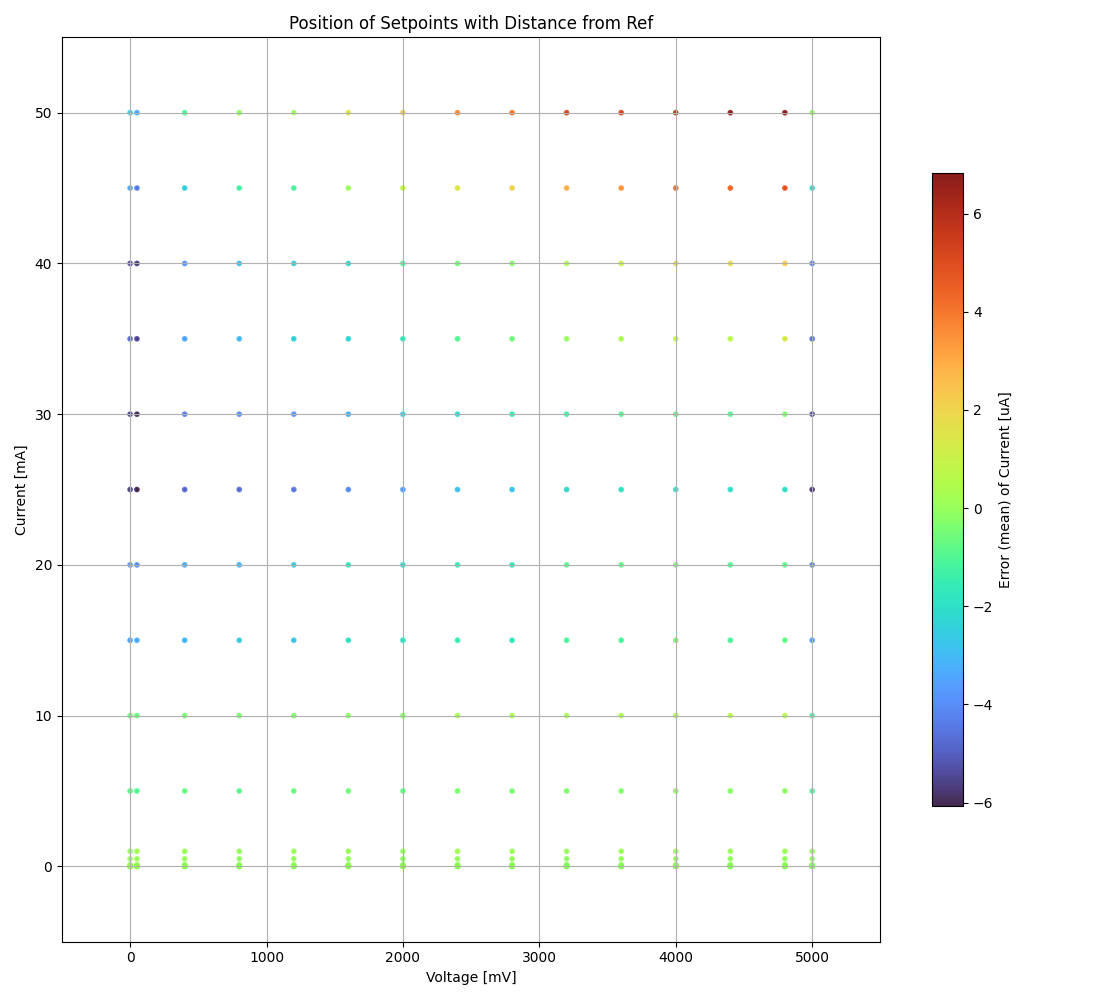
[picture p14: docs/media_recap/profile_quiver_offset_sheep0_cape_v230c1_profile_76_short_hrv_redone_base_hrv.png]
hrv_profiled


### Virtual Harvester

- either harvest right away (MPPT, constant voltage) -> iv-stream
- or defer the harvesting by sampling ivsurface / curves (or isc & voc)
- configurable by 10 parameters

Implemented harvest-algorithms (& parameters)

| Algorithm | Parameters                                          |
|-----------|-----------------------------------------------------|
| ivcurve   | window size, v_min, v_max, wait-cycles, direction   |
| isc & voc | wait-cycles                                         |
| v-const   | voltage                                             |
| mppt-voc  | setpoint, t_interval & t_duration (voc-measurement) |
| mppt-po   | v_min, v_max, v_step, t_interval                    |

### Emulator Circuit

- lowest resolution, set by software / resistor

  - DAC 19.53 uV
  - ADC 190 nA
  - voltage set in < 8 us

- switches and traces get compensated on PCB (Feedback is coming from target-header pin)

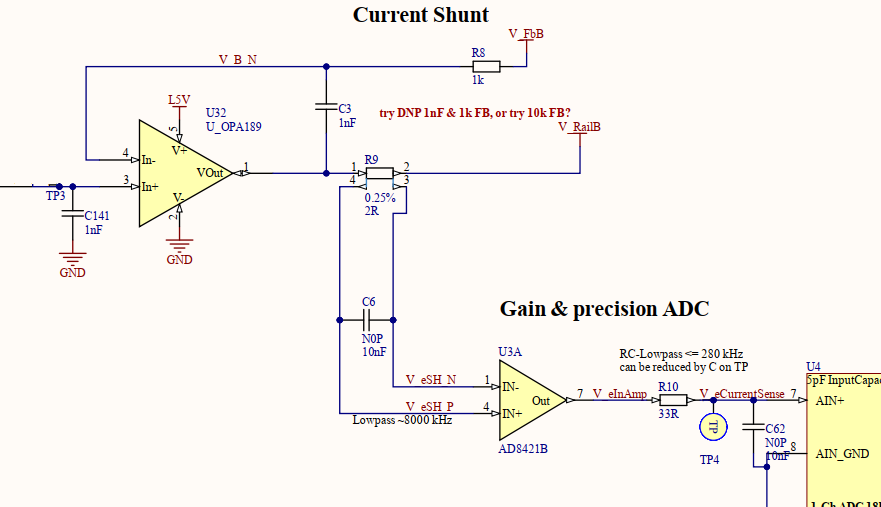
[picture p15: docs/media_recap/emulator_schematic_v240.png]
schematic_emu


#### Performance

- at 50 mA around 3.8 V are usable without large error

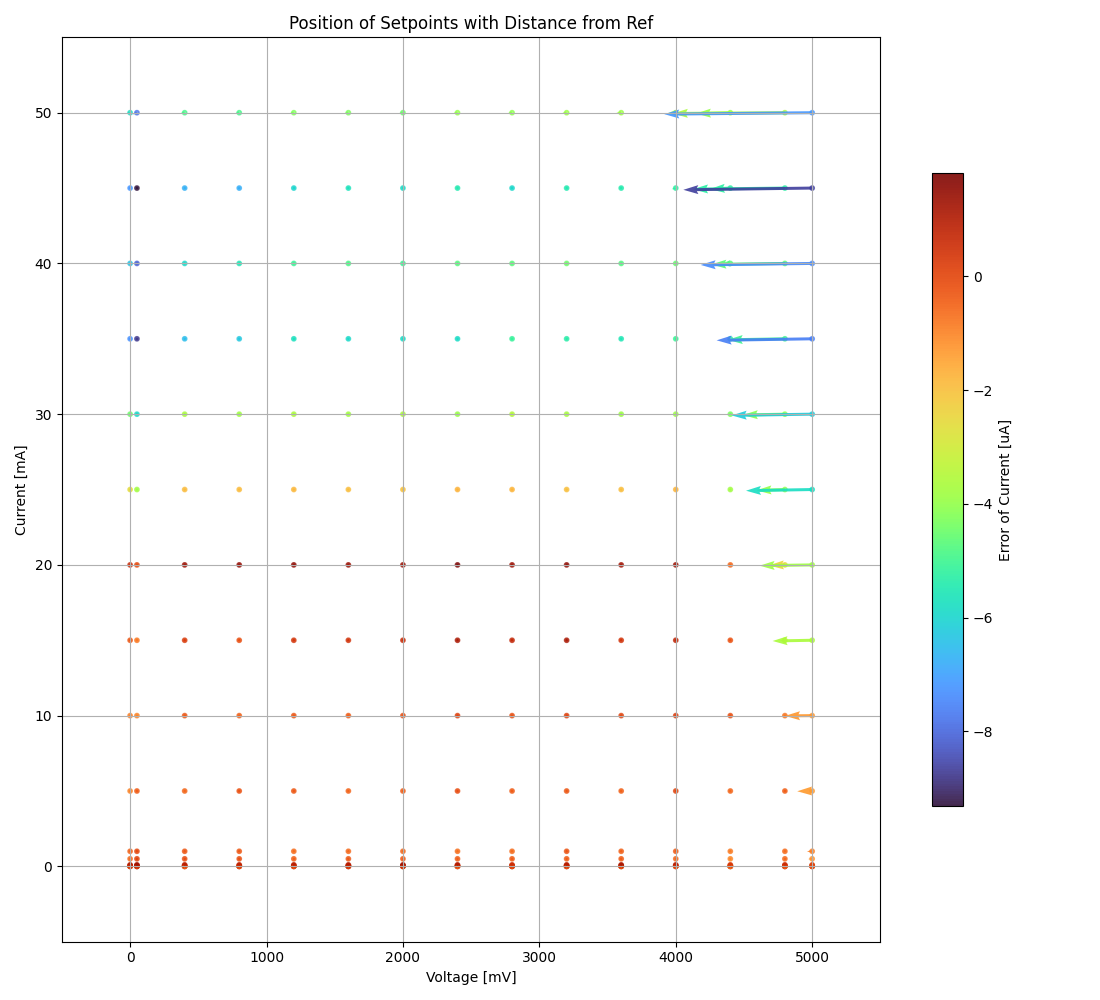
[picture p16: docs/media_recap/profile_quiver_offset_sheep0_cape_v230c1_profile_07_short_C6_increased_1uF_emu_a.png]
emu_profiled


### Virtual Source

#### General  Features

- integrated into PRU, calculated and updated at 100 kHz
- fully customizable per yaml-parameter-set (29+ parameters)

  - predefined sets by name ie. "virtsource: BQ25504s" for the BQ-Regulator with additional schmitt-trigger for pwr-good
  - neutral parameter-set is base -> direct throughput
  - inherit from existing parameter-sets -> only add altered parameters in new set

- emulator can either record output or intermediate voltage (storage cap)
- naming: source = harvester + converter
- design enables users to automate testing of harvesting-setup e.g. by sweeping through parameters like storage-cap-size

schematic_vsource2

#### Examples for predefined parameter-sets

- direct throughput of traces
- simple diode + capacitor
- buck-boost-converter (e.g. BQ25570) including the power-good-signal and efficiencies of underlying converters
- buck-converter (BQ25504)

#### Input

- oneway, imagine a perfect diode at the start so no current can flow back
- diode voltage-drop can be configured from 0 to x Volt
- maxima for input voltage and current (power limit)

#### Boost-Converter, optional

- enable minimum threshold voltage for input
- disable maximum threshold for boost-output (intermediate voltage)
- efficiency factor with 2D-LUT (12×12),

  - depending on input voltage & current
  - thresholds are configurable in 2^n steps
  - voltage divisions are linear, depending on lowest threshold
  - current-divisions are log2, also depending on lowest threshold
  - example: voltage threshold n=7 is setting first array boundary to 2^7 = 128 uV, so lut[0] is for V < 128 uV, lut[1] is for 128 to 256 uV

#### Capacitor, optional

- capacitance from 1 nF to 1 F
- initial voltage
- leakage current
- switchable output, hysteresis with checks at defined intervals
- power-good-signal with hysteresis either in intervals or immediate (schmitt-trigger)

#### Buck-Converter, optional

- fixed output voltage
- ldo-drop-voltage, alternatively working like a diode when buck is off or intermediate voltage is below output-voltage + drop-voltage
- efficiency factor with 1D-LUT

  - depending on output-current
  - threshold is configurable in 2^n-steps
  - current-divisions are log2, depending on lowest threshold
  - example: current threshold n=5 is setting first array boundary to 2^5 = 32 nA, so lut[0] is for I < 32 nA, lut[1] is for [32, 64] nA, lut[2] is for [64, 128] nA

#### Switchable output

- simulated external Capacitor - should be set to buffer size of target: fast transients can't be fully monitored by shepherd

### GPIO to Target

GPIO Implementation

| Pin-Name | 2nd FN   | Ctrl      | Dir       | Pru-Mon |
|----------|----------|-----------|-----------|---------|
| GPIO 0   |          | dir1-pin  | Rx-Tx     | yes     |
| GPIO 2   |          | dir1-pin  | Rx-Tx     | yes     |
| GPIO 3   |          | dir1-pin  | Rx-Tx     | yes     |
| GPIO 1   |          | dir1-pin  | Rx-Tx     | yes     |
| GPIO 4   |          |           | always RX | yes     |
| GPIO 5   |          |           | always RX | yes     |
| GPIO 6   |          |           | always RX | yes     |
| GPIO 7   | uart rx  |           | always RX | yes     |
| GPIO 8   | uart tx  | dir2-pin  | Rx-Tx     | yes     |
| BAT OK   |          |           | always TX | (yes)   |
| SWD1 CLK | jtag TCK |           | always TX |         |
| SWD1 IO  | jtag TDI | pDir1-pin | Rx-Tx     |         |
| SWD2 CLK | jtag TDO |           | always TX |         |
| SWD2 IO  | jtag TMS | pDir2-pin | Rx-Tx     |         |

#### Sampling frequency of gpio-monitor

- legacy	   -> 160 kHz … up to 1.5 … 2.9 MHz
- intermediate -> relatively stable 4.03 MHz, min: 602 kHz, max: 4.55 MHz
- current code … tbd

#### Electrical side

- translator: 74LVC2T45GS
- 470 R line resistor and 100k PU on both sides
- analog switch: PI5A4158, ~ 34 pF line-capacitance, [< 20 nA leakage]
- previous switch: > 300 pF, < 1 nA leakage

#### Performance-data

- not available atm
- previous switch limited to ~ 200 kHz
- capacitance on line is ~ 1/10, resistance ~ 1/2 -> 2 MHz should be fine

#### Logging of system parameters while recording

- io calls
- cpu usage
- nw usage
- ram usage

### Time-sync

- shepherd V1 started with +- 2.4 us error
- improvements on PRU-Level helped to push the boundaries
- also important: hardware-accelerated network-switch
- tbd: cisco-switch in TUD has layer 3 routing and >doubled spec -> could improve sync

#### Error between nodes

- q95% is < +- 200 ns

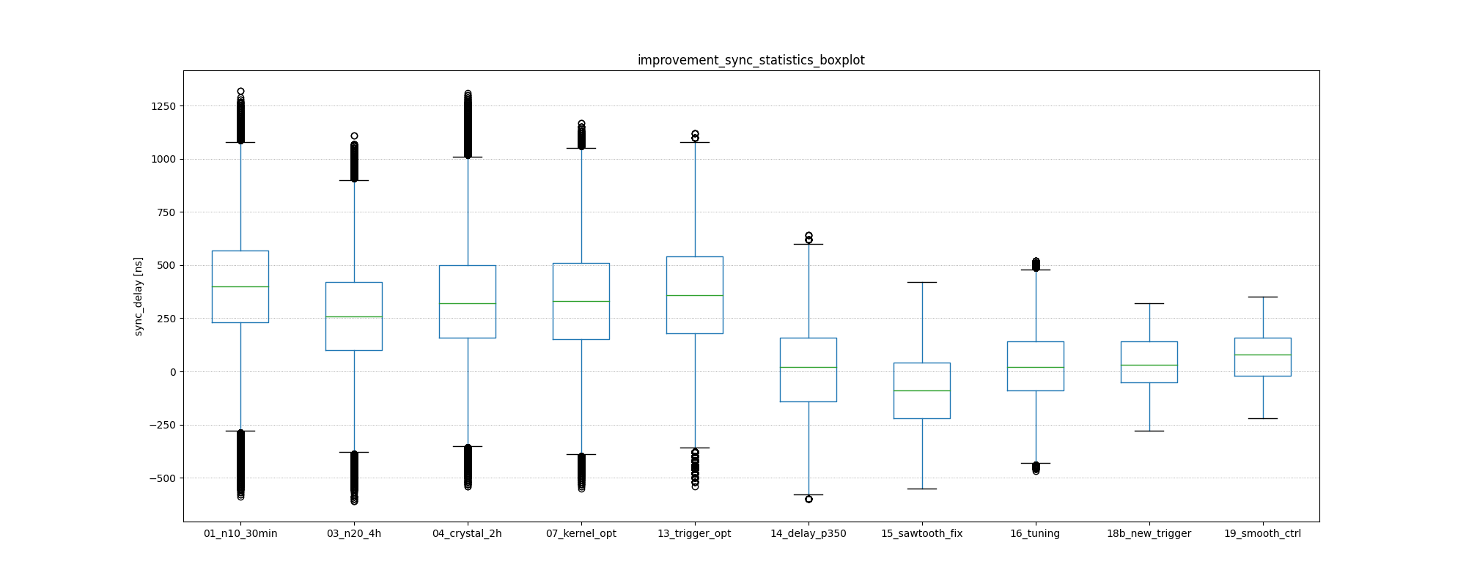
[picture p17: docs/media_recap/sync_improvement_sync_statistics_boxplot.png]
sync_improvement


#### Jitter between Trigger-Events (local)

- q95% is around +- 50 ns (10 pru cycles)

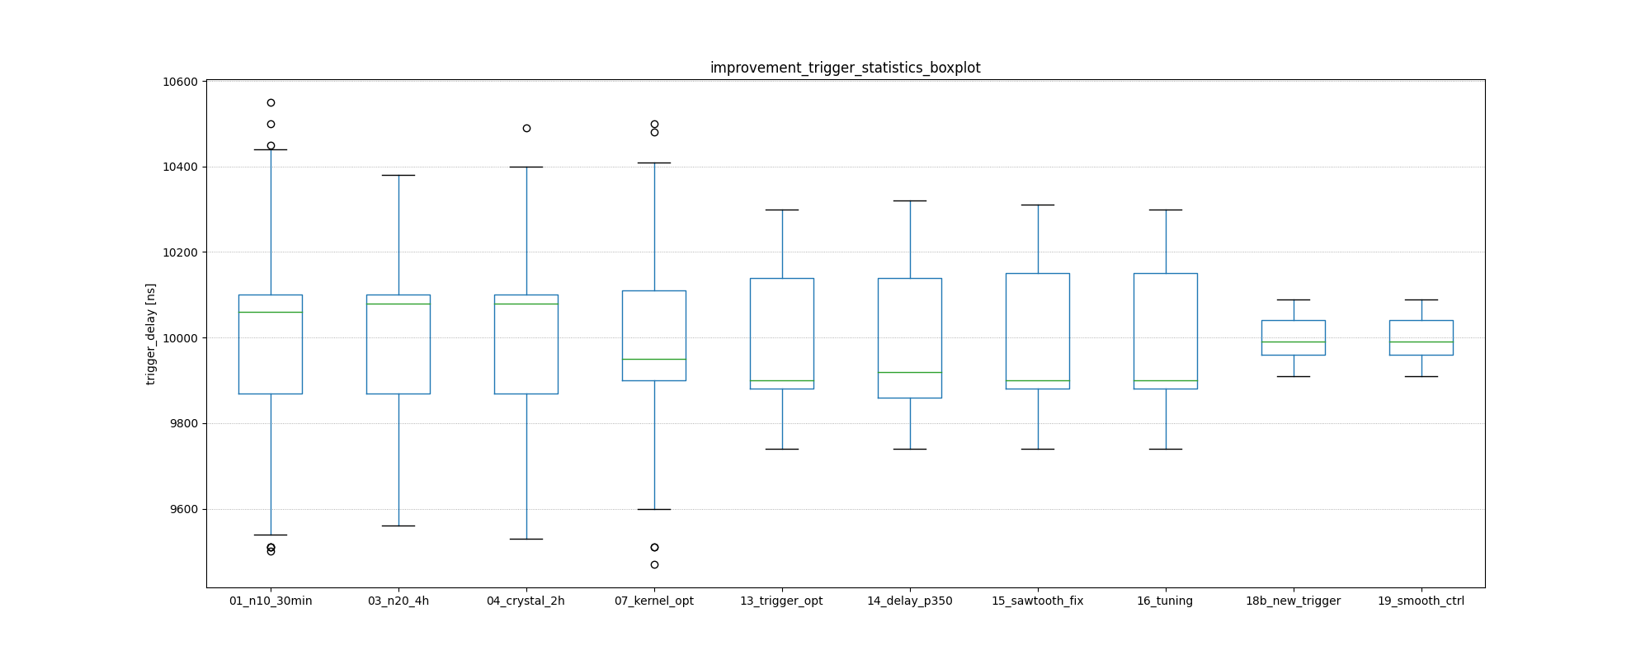
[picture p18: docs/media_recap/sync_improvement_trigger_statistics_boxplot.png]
trigger_improvement


### User-Tools

- API for py and cli
- read, write (and generate) shepherd-files
- check for plausibility and validity
- extract data and metadata, convert, downsample, plot, repair

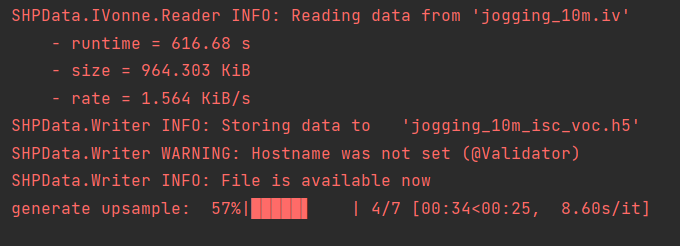
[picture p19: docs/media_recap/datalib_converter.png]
data_progress


#### Plotting

Multiplot for different harvesting strategies: ivcurve, isc / voc, voc-harvester and optimal po-harvester:

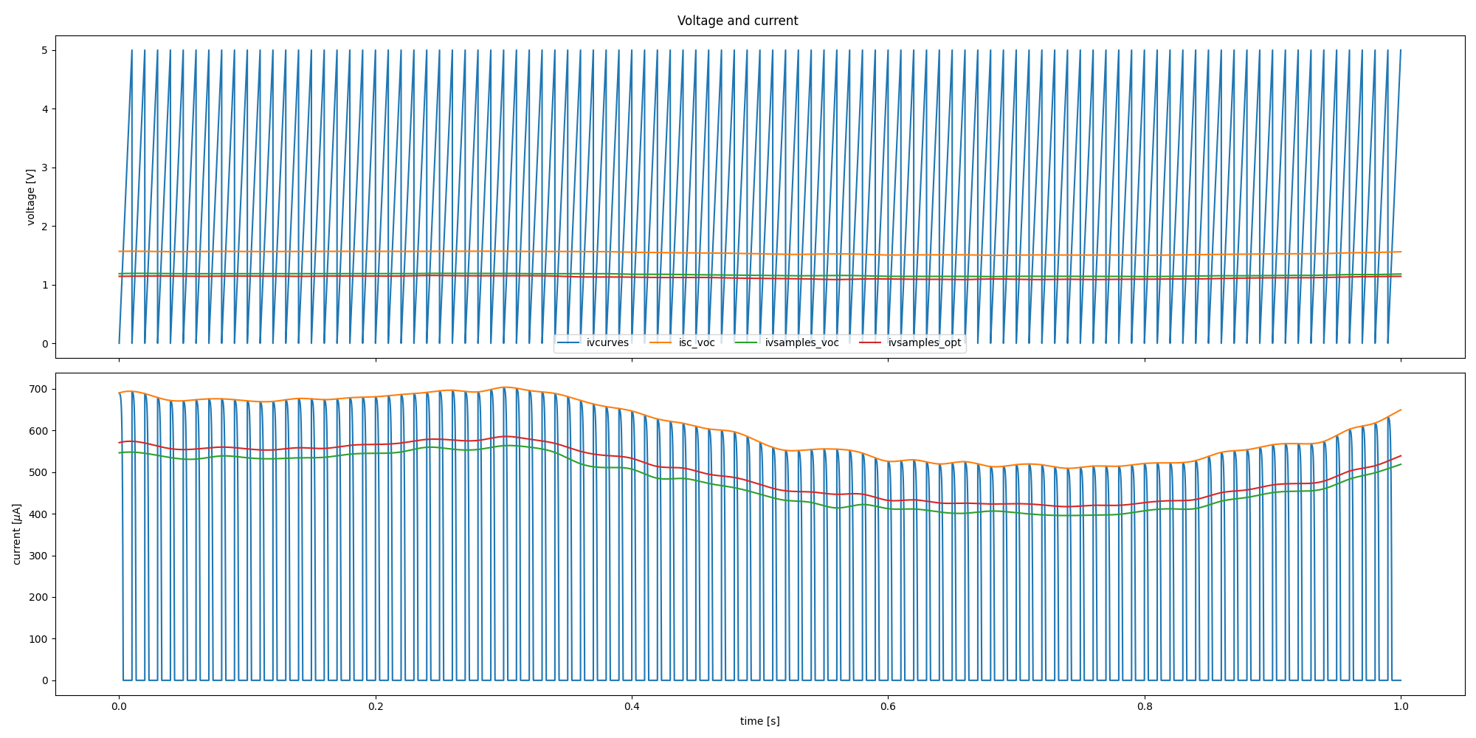
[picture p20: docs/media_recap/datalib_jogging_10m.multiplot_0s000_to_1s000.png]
data_plot


### TODO

- test-performance - MEAN error current
- add Overview-Schematic at the beginning

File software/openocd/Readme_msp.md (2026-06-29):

# Programmer / Debugger for the MSP430

## Current state

- [MSP on Riotee can be softbricked](https://github.com/NessieCircuits/Riotee_ProbeSoftware/issues/10)
- PRU-programmer on shepherd is a lite-version of Riotee-Probe
  - 2022-09: [pru-programmer](https://github.com/nes-lab/shepherd/tree/main/software/firmware/pru0-programmer) was designed
  - 2023-01: [riotee-programmer](https://github.com/NessieCircuits/Riotee_ProbeSoftware/tree/main/firmware/src) was designed (more generalized approach)
  - 2026-06: riotee-code was merged into shepherd - with minor adjustments to the protocol
- support via OpenOCD would be perfect
  - broad support for targets and programmers (even Linux-GPIO)
  - it allows connecting via GDB
  - BUT SBW is too niche, timing-sensitive and different from ARM/SWD in OpenOCD
- there are no TI tools supporting ARM (beaglebone or raspberry pi)
- mspdebug exists as the next best thing to OpenOCD
  - BUT relies mostly on programmers (i.e. [rpi-project](https://github.com/jonathangjertsen/rpi-msp430))
  - PIF (parallel port) programmer for GPIO is available, BUT it only supports JTAG
  - it also seems
- Putting a raspberry pico in between as a programmer would also work
  - Pi-Pico-Sbw https://github.com/bigjosh/pi-pico-sbw
  - could leverage https://github.com/bigjosh/pi-pico-sbw/blob/main2/mpy/sbw_native.c

### OpenOCD

- simplelink (not our targets)
  - https://software-dl.ti.com/msp430/msp430_public_sw/mcu/msp430/simplelink-openocd/latest/index_FDS.html
- TI OpenOCD (also not our targets)
  - https://software-dl.ti.com/ccs/esd/vscode/ti-embedded-debug/ti-openocd.html
  - https://github.com/TexasInstruments/ti-openocd
- official mirror: https://github.com/openocd-org/openocd/
- adapt SBW to openOCD?
  - analog to https://github.com/arduino/OpenOCD/blob/c404ff5d3a2ec568daa106455845dd403b08dab4/src/target/adi_v5_swd.c
  - patchguide https://openocd.org/doc-release/doxygen/patchguide.html
  - probably not feasible

### MSPDebug

https://dlbeer.co.nz/mspdebug/
https://github.com/dlbeer/mspdebug

Olimex Programmers
- MSP430-JTAG-TINY
  - https://www.olimex.com/Products/MSP430/JTAG/MSP430-JTAG-TINY-V2/
- MSP430-JTAG-ISO
  - https://www.olimex.com/Products/MSP430/JTAG/MSP430-JTAG-ISO/ (obsolete)
  - https://www.olimex.com/Products/MSP430/JTAG/MSP430-JTAG-ISO-MK2/

There seems to be a [device_gpio & device_bp](https://github.com/dlbeer/mspdebug/tree/v0.26/drivers/pif.h)
- pif is parallel port, bp is bus-pirate
- device_gpio uses [/sys/class/gpio](https://github.com/dlbeer/mspdebug/tree/v0.26/drivers/pif.c#L445)
- HOW? `mspdebug --help` does not list GPIO. change was 12 years old, but apt-version is 13 years old ...
- according to [this website](https://rpm.pbone.net/manpage_idpl_29179731_numer_1_nazwa_mspdebug.html) only JTAG is supported for GPIO-device, proposed call: `mspdebug gpio -d "tdi=7 tdo=8 tms=9 tck=4"`
- **it seems all 3 devices in pif.c lack SBW-support

There is a [PR for bitbanging via FTDI](https://github.com/dlbeer/mspdebug/pull/118) that could be adapted to linux-GPIO.

Compile

```Shell
# sudo apt install libusb-1.0-0-dev
sudo apt install libusb-dev
cd
git clone https://github.com/dlbeer/mspdebug
# git clone https://github.com/dlbeer/mspdebug/tree/v0.26
cd mspdebug
git checkout tags/v0.26
make WITHOUT_READLINE=1
# ~ 3min
sudo make install WITHOUT_READLINE=1
# /usr/local/lib//mspdebug
/usr/local/bin/mspdebug --version
```

TODO:
- adapt gpio-driver of openOCD for mspdebug?
- sbw_transport
- sbw_jtag
- sbw_device
- _linuxgpio

## Program

sudo shepherd-sheep -v target-power --gpio-pass --target-port=A

sudo shepherd-sheep program -pA -m2 --mcu-type msp430 /var/shepherd/content/fw/nes_lab/msp430_deep_sleep/build.hex
sudo shepherd-sheep program -pA -m2 --mcu-type msp430 /opt/shepherd/hardware/tests_manual/msp430_testable.hex

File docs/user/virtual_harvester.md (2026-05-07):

# Virtual Harvester

:::{note}
TODO: WORK IN PROGRESS
:::

## IVSurface - Transition-Cutout

The analog frontend needs a bit more than a cycle to handle large 5 V transitions.
Solar cells add extra capacitance to the frontend and make the transition slower.

The virtual harvester can cutout these transition periods to avoid recording unwanted capacitive effects.

Using the `cutout_cycles` and `enable_automatic_cutout` parameters is mostly meant to avoid post-processing before using the traces for emulation.
To avoid interfering with the window_size-calculations, this cutout happens at the beginning of the IVCurve-window and will influence V_OC or I_SC values (depending on `rising` parameter).

Automatic mode works by

- gets activated during reset of voltage-ramp
- hold the previous adc-samples during that transition
- check if transition is complete to disable cutout
  (i.e. if rising of voltage stops for a falling ramp)
- compensation for noise via `cutout_cycles`-parameter acting as buffer
  (forgiving that number of cycles that can violate condition before ending the cutout)

### Example 1 - Solar with Rising Ramp

After restarting the voltage ramp (jumping down to 0 V), the current is higher than it should.
As a result, the power-trace has an undesired spike.
This behavior varies with the cell-type and illumination and hints at some capacitive load on the cell.
Note that the 0 V level (I_SC) is lost for this mode, because it is hidden in the transition-period or the cutout.

There is another unwanted effect that raises the Voltage slightly higher when the ramp crosses V_OC.
Due to the design of the harvesting-circuit the recorded voltage shouldn't rise higher than V_OC.

Without cutout:

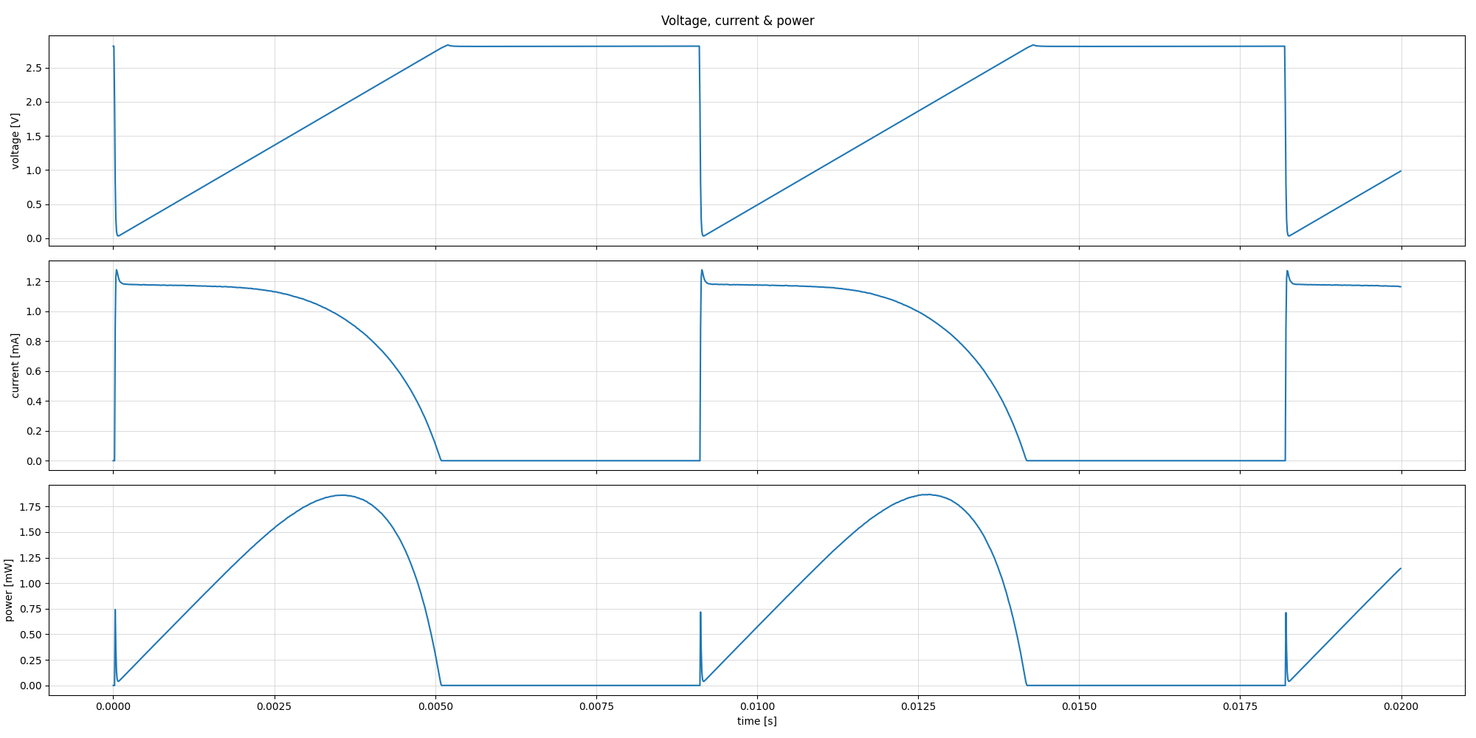
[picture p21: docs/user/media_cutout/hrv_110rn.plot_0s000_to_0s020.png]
iv110-recording without cutout


With automatic cutout (+3 buffer cycles):

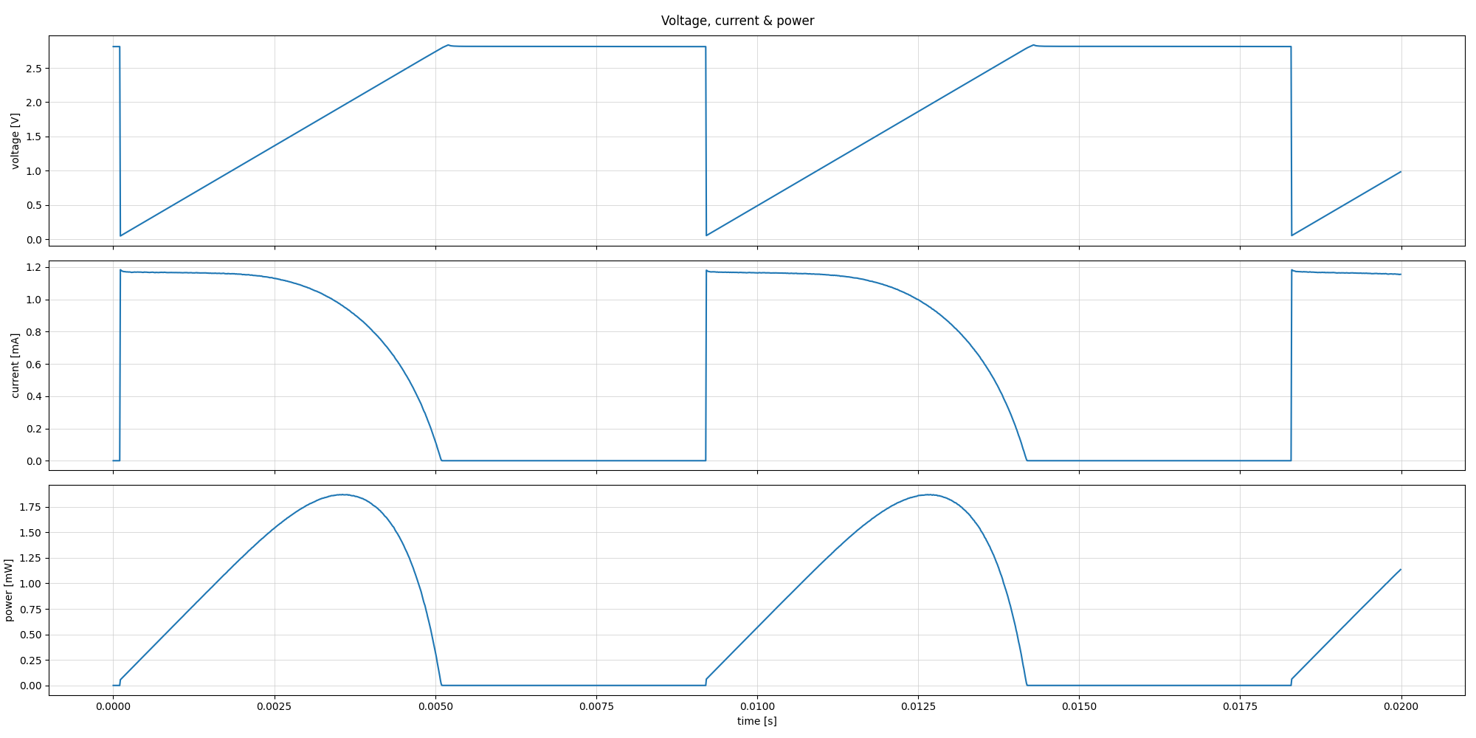
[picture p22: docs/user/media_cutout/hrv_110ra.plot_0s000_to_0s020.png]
iv110-recording with automatic cutout


### Example 2 - Solar with Falling Ramp

After restarting the voltage ramp (jumping up to 5 V), the voltage step is rounded off.
In addition, a small spike can be found in the power-trace.
The transition-phase (or cutout) usually falls in the part of the voltage ramp that is above the V_OC, so no information is lost.

Without cutout:

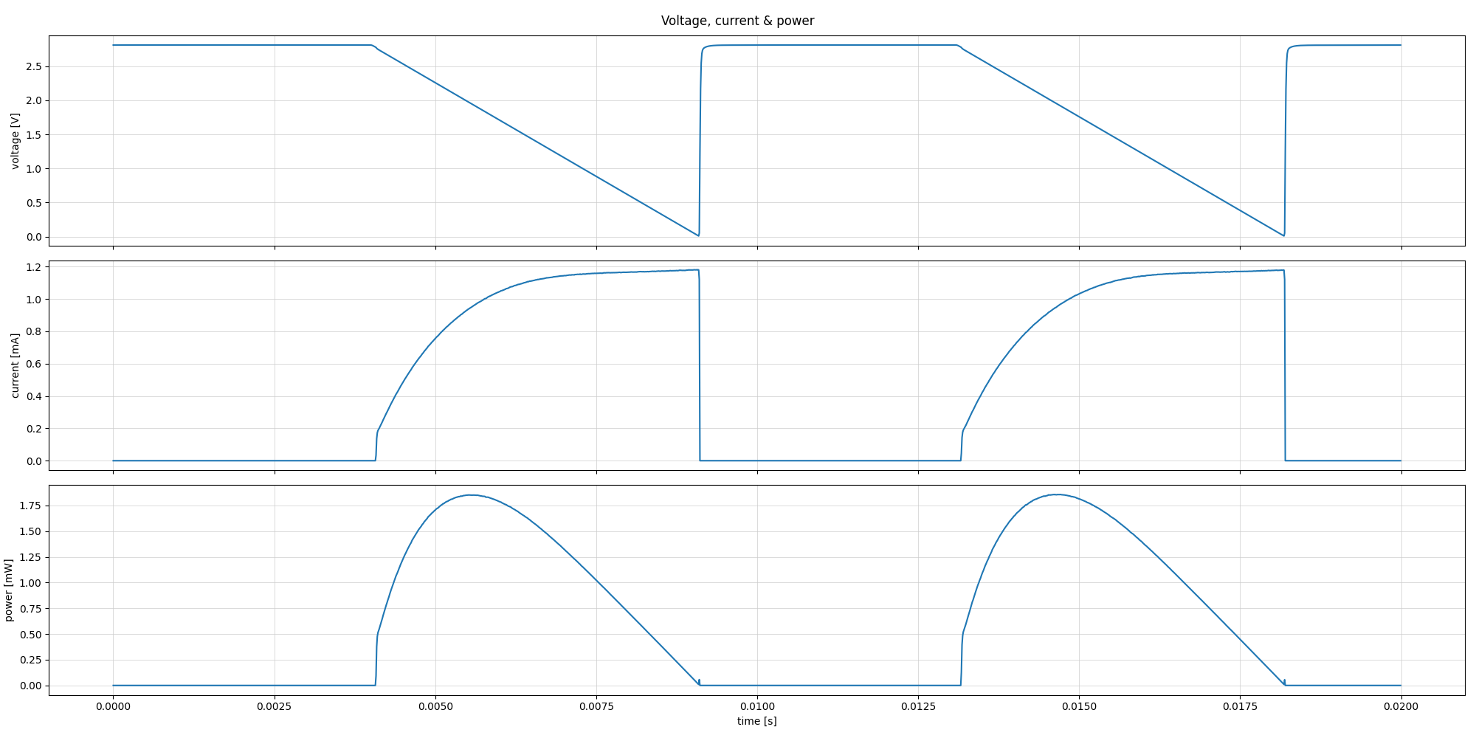
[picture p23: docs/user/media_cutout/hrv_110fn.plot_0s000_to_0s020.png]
iv110-recording without cutout


With automatic cutout (+3 buffer cycles):

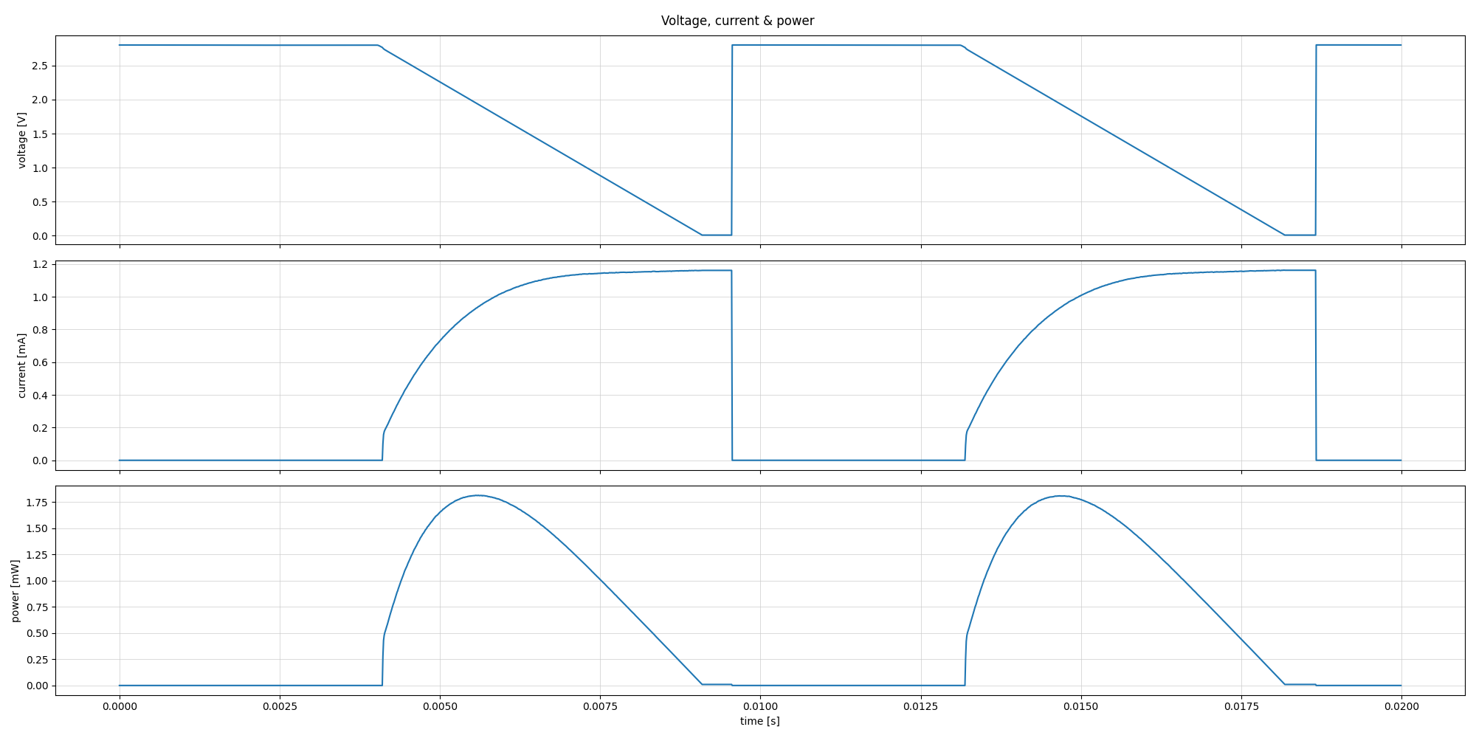
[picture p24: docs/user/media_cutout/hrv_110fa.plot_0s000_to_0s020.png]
iv110-recording with automatic cutout


Note that there is another unwanted effect when the falling voltage ramp crosses V_OC, the current stays lower than expected for the first samples.

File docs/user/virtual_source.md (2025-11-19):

# Virtual Source

While Shepherd v1 was built around an actual harvesting-IC the new version virtualizes most parts like the harvester, storage capacitors and voltage converters.
By switching to a software defined system the sourcing of energy becomes fully configurable.
The simulation loop runs in real-time with 100 kHz and allows to emulate a wide variety of voltage converter circuits.

:::{note}
TODO: WORK IN PROGRESS
:::

## Harvester

With one of the latest additions of sampling [IV-curves](https://en.wikipedia.org/wiki/Current%E2%80%93voltage_characteristic) during harvest, it is now possible to also emulate the actual harvesting. The harvesting options are

- constant voltage (CV)
- maximum power point tracking (MPPT) based on
  - open circuit voltage (MPPT_VOC), or
  - perturb & observe (MPPT_PO)

As an actual YAML-Example:

```yaml
- datatype: VirtualHarvesterConfig
  parameters:
    id: 1040
    name: mppt_voc
    description: MPPT based on open circuit voltage for solar
    inherit_from: neutral
    algorithm: mppt_voc
    setpoint_n: 0.76
    interval_ms: 100     # between measurements
    duration_ms: 1.2     # solar can overshoot when load is removed
    current_limit_uA: 5  # boundary for detecting open circuit in emulated version (working on IV-Curves)
```

### References

- [VirtualHarvesterConfig in corelib](https://github.com/nes-lab/shepherd-tools/blob/main/shepherd_core/shepherd_core/data_models/content/virtual_harvester.py)
- [Harvester-Fixtures in corelib](https://github.com/nes-lab/shepherd-tools/blob/main/shepherd_core/shepherd_core/data_models/content/virtual_harvester_fixture.yaml)
- [VirtualHarvester-Model in PRU](https://github.com/nes-lab/shepherd/blob/main/software/firmware/pru0-shepherd-fw/virtual_harvester.c)

## Emulator

```{figure} media/virtual_source_schemdraw.png
:name: vsource

fully customizable power supply toolchain
```

As an actual YAML-Example describing a simple diode & capacitor circuit:

```yaml
- datatype: VirtualSourceConfig
  parameters:
    id: 1011
    name: diode+capacitor
    description: Simple Converter based on diode and buffer capacitor
    inherit_from: neutral
    V_input_drop_mV: 300  # simulate input-diode
    storage:  # primary storage-Cap
      name: Capacitor_10uF_10.0V
```

## Sim-Example 1

Setup:

- TI BQ25504 (with default slow pwr-good & fast schmitt-trigger)
- I_inp = 100 uA @ 1200 mV
- I_out = 1 mA (active MCU), 200 nA (sleep)
- V_power_good = 2.2 V

The only difference between the two runs is the altered power-good-circuit. The original BQ25504 is too slow to inform the MCU about the low energy level and therefore the MCU drains the capacitor. Note the small voltage drop in the first picture. The BQ disconnects the output for very low voltages and reconnects it on a certain voltage. The drop is caused by the simulated output-capacity.

```{figure} media/vsource_sim_BQ25504_1200mV_5000ms.png
:name: vsource_sim_bq

BQ25504 with default slow pwr-good
```

```{figure} media/vsource_sim_BQ25504s_1200mV_5000ms.png
:name: vsource_sim_bqs

BQ25504 with fast schmitt-trigger
```

[Source](https://github.com/nes-lab/shepherd-tools/blob/main/shepherd_core/examples/vsource_simulation.py)

## Sim-Example 2

Setup:

- diode + cap circuit with immediate schmitt-trigger for power-good
- I_inp = 100 uA @ 1200 mV
- I_out = 1 mA (active MCU), 200 nA (sleep)
- V_power_good = 2.2 V

The input-voltage is too small to charge the circuit up to V_power_good, so the capacitor is slowly discharging from its own leakage and the MCUs current-draw during sleep.

```{figure} media/vsource_sim_diode+capacitor_1200mV_500ms.png
:name: vsource_sim_diode_cap

diode + cap circuit with fast schmitt-trigger for power-good
```

[Source](https://github.com/nes-lab/shepherd-tools/blob/main/shepherd_core/examples/vsource_simulation.py)

### References

- [VirtualSourceConfig in corelib](https://github.com/nes-lab/shepherd-tools/blob/main/shepherd_core/shepherd_core/data_models/content/virtual_source.py)
- [Source-Fixtures in corelib](https://github.com/nes-lab/shepherd-tools/blob/main/shepherd_core/shepherd_core/data_models/content/virtual_source_fixture.yaml)
- [VirtualSource-Model in PRU](https://github.com/nes-lab/shepherd/blob/main/software/firmware/pru0-shepherd-fw/virtual_converter.c)
- [VirtualSource-Model in corelib](https://github.com/nes-lab/shepherd-tools/tree/main/shepherd_core/shepherd_core/vsource)
- [example of a VirtualSource-Simulation](https://github.com/nes-lab/shepherd-tools/blob/main/shepherd_core/examples/vsource_simulation.py)

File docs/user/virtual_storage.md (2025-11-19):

# Battery Model for Shepherd

## Basis

The model is based on the electrical model introduced in [_An Accurate Electrical Battery Model Capable of Predicting Runtime and I–V Performance_](https://rincon-mora.gatech.edu/publicat/jrnls/tec05_batt_mdl.pdf).

The circuit diagram of the electrical model is shown here:
electrical circuit model

The model uses:

- a capacitor (`C_capacity`) to model the `State of Charge` (SoC)
- a controlled voltage source to model the relation of SoC to open-circuit voltage
- a series resistor to model the current dependent voltage drop
- two RC elements to model transient voltage effects
- a resistor to model self-discharge (however, they later omit this, deeming it negligible)

The component values depend on the SoC through a set of equations:
electrical circuit model equations

These parameters model a specific battery and are provided by the authors.

## Kinetic Battery Model

The electrical model described above was used as a basis for the more complex hybrid model introduced in [_A Hybrid Battery Model Capable of Capturing Dynamic Circuit Characteristics and Nonlinear Capacity Effects_](https://digitalcommons.unl.edu/cgi/viewcontent.cgi?article=1210&context=electricalengineeringfacpub).

This model introduces the so called `rate capacity` effect which causes temporary changes in available capacity due to chemical effects that occur when a current is applied.
Since the corresponding formulas are rather complex, implementing them on the PRU is unfeasible.

However, the authors also parameterize their model and provide parameter values for both a Lithium-Polymer [(PL-383562)](https://www.batteryspace.com/prod-specs/pl383562.pdf) and a Lead-Acid [(LEOCH LP12-1.2AH)](https://www.leoch.com/pdf/reserve-power/agm-vrla/lp-general/LP12-1.2.pdf) battery.
A subset of these parameters can be used to configure the electrical model and extend the PRU implementation.
Shepherd keeps the whole parameter-set for a future-proof basis were the models can be extended when the computing platform changes.

Experiments showed that a broad range of configurations can be covered by this model:

- various capacitors (ideal, Tantal, MLCC inkluding Bias-Effect)
- lithium batteries (LiPo, LiOn, LiFe)
- lead acid

## Modifications

For a more generalized `virtual storage`, the following extensions were implemented for `KiBaM`:

- support the rate capacity effect and transients during charging (the original focuses only on discharge)
- self discharge was added as it is relevant for capacitors
- a 0 % SoC will let the voltage break down to 0
- future extension: include DC-bias effect, see section below

Due to processing-constraints the following modifications are made implementing the model on the PRU:

- the transient effects (e.g. the two RC elements, eq. 4 - 7) are omitted
- the equations (2, 3) for the open-circuit voltage and series resistor are replaced by lookup-tables (LuTs) which are generated from the model equations ahead of time
  - future plan: the quantized output voltage (due to the 128-entry LuT) may be smoothed via interpolation
- the capacitor is modeled discretely: `V_soc(t + dt) = V_soc(t) - (1 / C_capacity) * I_batt * dt`

## Comparison of Models

For qualifying the implementation a set of models was used to show differences in behavior:

- `KiBaM` is the model presented in the mentioned paper
- `KiBaMPlus` was extended to support the rate capacity effect and transients during charging (the original focuses only on discharge). It also added self discharge via a parallel leakage resistor
- `VirtualStorage` is the stripped down PRU-Version (see Modifications listed above)
- `ShpCap` is the (now) legacy implementation of the energy storage for shepherd

These models are capable of receiving and simulating the same parameter-sets

- `LiPo` battery with 10 mAh & 3.7 V nominal voltage
- ~~`Lead Acid` battery with 10 mAh & 12 V nominal voltage (6 cells)~~
- an ideal `Capacitor` with 10 F (to be comparable) and a rated Voltage of 4.2 V

For each a set of experiments was constructed to display the individual behavior

- a 20 Ohm resistive load
- pulsed charging
- ~~pulsed discharging~~ (similar to resistive load)
- ~~self discharge~~

The python scripts can be found in [shepherd_core/examples/simulations/vstorage.py](https://github.com/nes-lab/shepherd-tools/blob/dev/shepherd_core/examples/simulations/vstorage.py).

### Resistive Load

Putting a 20 Ohm load on the capacitor shows no surprises - all 4 models match in behavior:

comparison cap resistive load

Differences start to show when looking at the LiPo battery:

comparison lipo resistive load

The KiBaM-based models both match in behavior and show the voltage curve of a typical lithium battery.
Even the stripped PRU-model (`VirtualStorage`) is close by, but lacks the rate capacity effect and is therefore missing the voltage drop.
The old shepherd capacitor (`ShpCap`) was not designed to mimic a battery and misbehaves completely.

### Pulsed Charging

Charging a capacitor with pulsed 100 mA is again covered by all 4 models:

comparison cap pulsed_charging

Differences show again when looking at the LiPo:

comparison bat pulsed_charging

While the old shepherd capacitor (`ShpCap`) was not designed to mimic a battery and can be ignored, the other models show interesting behaviors.
This time the simple KiBaM and the stripped PRU-Model (`VirtualStorage`) match, as both don't support transients during charging.
Looking at the voltages a non-linear trend shows, typical for lithium batteries.
In addition `KiBaMPlus` handles the rate capacity effect during charging, which shows as voltage increase while current is flowing.

## DC-Bias Effect

Some capacitors like MLCC-variants show a variable capacity, depending on the voltage they are used.
Small packages with high capacity are particularly susceptible to this DC-bias effect.
The datasheet of the JMK316ABJ107ML a 100 uF X5R MLCC with a rated voltage of 6.3 V show a capacity decrease of 80 % when run at the rated voltage.

dc-bias

In comparison to an ideal capacitor the charge- and discharge-curves differ substantially.
We were able to verify the datasheet for that specific capacitor by measuring both curves and plotting the datasheet data next to it (`direct`).
As an experiment the `VirtualStorage` PRU-Model (called `BatteryModel` in plot) was adapted to contain this effect in the SoC-LuT.

:::{note}
TODO: WORK IN PROGRESS
The DC-bias effect will be included in the near future. More measurements and research are needed to offer a parameter-set.
:::

## References

- parameters for the config can be found as [data-model in the core-tool](https://github.com/nes-lab/shepherd-tools/tree/main/shepherd_core/shepherd_core/data_models/content)
  - a fixture creation script and the fixtures itself are in the same directory
- the virtual storage for the testbed is implemented in c and [part of the PRU-firmware](https://github.com/nes-lab/shepherd/tree/main/software/firmware/pru0-shepherd-fw)
- the 1-to-1 simulation-models are part of the [python vSource-implementation](https://github.com/nes-lab/shepherd-tools/tree/main/shepherd_core/shepherd_core/vsource)
- simulation-experiments are kept in the [examples-directory of the core-tool](https://github.com/nes-lab/shepherd-tools/tree/main/shepherd_core/examples/simulation)
- performance analysis between python-models, c-code and actual are [documented here](https://github.com/nes-lab/shepherd/blob/main/software/debug_compare_vsources/README.md)

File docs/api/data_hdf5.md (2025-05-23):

# Shepherd-Data - HDF5 Reader & Writer

:::{note}
TODO: WORK IN PROGRESS
:::

These two classes allow the user to read and write shepherds hdf5-files.
For more details about the data-format you can read:

- doc for [](../user/data_format.md)
- [Reader-source](https://github.com/nes-lab/shepherd-tools/blob/main/shepherd_core/shepherd_core/reader.py) in core-lib
- [Reader-source](https://github.com/nes-lab/shepherd-tools/blob/main/shepherd_data/shepherd_data/reader.py) in data-module (Inherits from core-reader)
- [Writer-source](https://github.com/nes-lab/shepherd-tools/blob/main/shepherd_core/shepherd_core/writer.py)

## Usage-Example

This basic example can read & print some metadata from a hdf5-file.

```python
import shepherd_data as sd

with sd.Reader("./hrv_sawtooth_1h.h5") as db:
    print(f"Mode: {db.get_mode()}")
    print(f"Window: {db.get_window_samples()}")
    print(f"Config: {db.get_config()}")
```

## Reader

```{eval-rst}
.. autoclass:: shepherd_data.Reader
    :members:
    :inherited-members:
```

## Writer

```{eval-rst}
.. autoclass:: shepherd_data.Writer
    :members:
    :inherited-members:
```

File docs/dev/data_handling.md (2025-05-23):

# Data handling

## Data Acquisition

Data is sampled/replayed through the ADC (`TI ADS8691`) and DAC (`TI DAC8562T`). Both devices are interfaced over a custom, SPI-compatible protocol. For a detailed description of the protocol and timing requirements, refer to the corresponding datasheets. The protocol is bit-banged using the low-latency GPIOs connected to PRU0. The transfer routines itself are [implemented in assembly](https://github.com/nes-lab/shepherd/blob/main/software/firmware/lib/src/spi_transfer_pru.asm).

## PRU to host

Data is sampled and bidirectionally transferred between PRUs and user space in buffers. These buffers correspond to sections of a continuous area of memory in DDR RAM to which both PRUs and user space application have access. This memory is provisioned through `remoteproc`, a Linux framework for managing resources in an AMP (asymmetric multicore processing) system. The PRU firmware contains a so-called resource table that allows to specify required resources. We request a carve-out memory area, which is a continuous, non-cached area in physical memory. On booting the PRU, the `remoteproc` driver reads the request, allocates the memory and writes the starting address of the allocated memory area to the resource table, which is readable by the PRU during run-time. The PRU exposes this memory location through shared RAM, which is accessible through the sysfs interface provided by the kernel module. Knowing physical address and size, the user space application can map that memory after which it has direct read/write access. The total memory area is divided into three distinct buffers for ivsamples, gpio-traces and pru-utilization-log.

The shared RAM approach is the fastest option on the BeagleBone, but still has some caveats. Writing from PRU-side to DDR RAM can be done within one cycle. The operation does not finish in that time, but does not block the PRU. Reading on the other hand can take several hundred cycles. In rare cases `> 4 us`, which equals 800 cycles or almost half the real-time window. For that reason the reading operation is done by PRU1, as it has more resources to spare. A future design should consider, that reading takes almost same time for 1 byte or 100 bytes.

:::{note}
This design will switch to a large cyclic buffer in the near future to reduce overhead (buffer exchanges) for the PRU.
:::

In the following we describe the data transfer process for emulation. Emulation is the most general case because harvesting data has to be transferred from a database to the analog frontend, while simultaneously data about energy consumption (target voltage and current) & gpio traces have to be transferred from the analog frontend (ADC) to the database.

The userspace application writes the first block of harvesting data into one of the (currently 64) buffers, e.g. buffer index 0. After the data is written, it sends a message to PRU0, indicating the message type (`MSG_BUF_FROM_HOST`) and index (0). The PRU0 receives that message and stores the index in a ringbuffer of empty buffers. When it's time, PRU0 retrieves a buffer index from the ringbuffer and reads the harvesting values (current and voltage) sample by sample from the buffer, sends it to the DAC and subsequently samples the 'load' ADC channels (current and voltage), overwriting the harvesting samples in the buffer. Once the buffer is full, the PRU sends a message with type (`MSG_BUF_FROM_PRU`) and index (i). The userspace application receives the index, reads the buffer, writes its content to the database and fills it with the next block of harvesting data for emulation.

### Data extraction

The user space code (written in python) has to extract the data from a buffer in the shared memory. Generally, a user space application can only access its own virtual address space. We use Linux's `/dev/mem` and python's `mmap.mmap(..)` to map the corresponding region of physical memory to the local address space. Using this mapping, we only need to seek the memory location of a buffer, extract the header information using `struct.unpack()` and interpret the raw data as numpy array using `numpy.frombuffer()`.

## Database

In the current local implementation, all data is locally stored in the filesystem. This means, that for emulation, the harvesting data is first copied to the corresponding shepherd node. The sampled data (harvesting data for recording and energy traces for emulation) is also stored on each individual node first and later copied and merged to a central database. We use the popular HDF5 data format to store data and meta-information.

See Chapter [](../user/data_format) for more details.

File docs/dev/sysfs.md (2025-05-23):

# SYSFS interface

The shepherd kernel module provides a user interface that exposes relevant parameters and allows control of the state of the underlying shepherd engine consisting of the kernel module and the firmware running on the two PRU cores. When the module is loaded, the interface is available under `/sys/shepherd`

## Basic Functionality

```{caution}
OUT OF DATA
```

- `state`: current state of the pru state-machine, mostly `idle` or `running`, plus some transitional states. Also used to control the PRU by setting `start` or `stop`.
- `mode`: can be either `emulator` or `harvester` and some debug-modes
- `n_buffers`: The maximum number of buffers used in the data exchange protocol
- `BUFFER_SAMPLES_N`: The number of samples contained in one buffer. Each sample consists of a current and a voltage value.
- `buffer_period_ns`: Time period of one 'buffer'. Defines the sampling rate together with `BUFFER_SAMPLES_N`
- `memory/address`: Physical address of the shared memory area that contains all `n_buffers` data buffers used to exchange data
- `memory/size`: Size of the shared memory area in bytes
- `pru_msg_box`: in and out message box to communicate with the PRUs

- `pru0_firmware` & `pru1_firmware`: allows to load a custom firmware, like `am335x-pru0-programmer-SWD-fw`

## Virtual Source

- `dac_auxiliary_voltage_raw`: secondary voltage channel of emulator and harvester. Set before starting the experiment if needed.
- `calibration_settings`: Load calibration settings. They are used in the virtual source algorithm.
- `virtual_converter_settings`: Settings which configure the emulator algorithm.
- `virtual_harvester_settings`: Settings for both the emulator and harvester mode

- `sync/error_sum`: Integral of PID control error
- `sync/error`: Instantaneous PID control error
- `sync/correction`: PRU Clock correction (in ticks, ~5ns) as calculated by the PID controller

## PRU Programmer

- `programmer/state`: state machine of the programmer firmware for the PRU, similar to the first state
- `programmer/protocol`: programming protocol (SBW or SWD)
- `programmer/datasize`: after writing the firmware to the shared ram, the actual size has to be written here
- `programmer/datarate`: in bits/second
- `programmer/pin_tck`: gpio pin of the PRU
- `programmer/pin_tdio`: see comment above
- `programmer/pin_tdo`: see comment above
- `programmer/pin_tms`: see comment above

```{note}
PRU0 must be loaded with a special firmware. The sheep-program does that automatically.
```

## References

- [sysfs in kernel module](https://github.com/nes-lab/shepherd/blob/main/software/kernel-module/src/sysfs_interface.c)
- [sysfs in sheep program](https://github.com/nes-lab/shepherd/blob/main/software/python-package/shepherd_sheep/sysfs_interface.py)

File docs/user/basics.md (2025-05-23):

# Basics

**Shepherd** is a testbed for battery-less cyber-physical systems, also publicly labeled as Internet of Things.
It allows to record harvesting conditions at multiple points in space over time.
The recorded data can be replayed to attached wireless sensor nodes (targets), examining their behavior under the constraints of spatio-temporal energy availability.

For a detailed, but slightly outdated description see our [Paper](https://wwwpub.zih.tu-dresden.de/~mzimmerl/pubs/geissdoerfer19shepherd.pdf) for shepherd version 1. Currently, version 2 is in use, which adds many improvements, while keeping the underlying idea.

A **shepherd** instance consists of a group of spatially distributed **shepherd** observers that are time-synchronized with each other.
Each **shepherd** observer consists of a single-board computer (SBC), the **shepherd** cape and a particular choice of connected targets.

Shepherd works in two key modes: [](#harvester) and [](#emulator).

## Time-synchronization

Generally, shepherd can be used on a single observer or without time-synchronization, for example, to measure the amount of energy that can be harvested in a particular scenario.
The more interesting feature however is that it enables to explore harvesting conditions across time and space, which is a crucial step towards collaboration and coordination of battery-less nodes.

For tethered settings, we propose to use the [Precision Time Protocol (PTP)](https://en.wikipedia.org/wiki/Precision_Time_Protocol).
It requires that all shepherd nodes are connected to a common Ethernet network with as little switching jitter as possible.
The BeagleBone has hardware support for PTP and Linux provides the necessary tools.

In mobile or long-range scenarios, it might not be feasible to connect the observer with Ethernet.
Instead, you can use the timing signal (PPS) from a GPS receiver.
We have designed a GPS capelet (hardware/capelet_gps) to easily connect a GPS receiver and provide all necessary software in our repository.

## Harvester

For recording a harvesting scenario, shepherd observers can be equipped with a harvesting transducer, e.g. a solar panel or piezo-electric harvester.
This transducer is connected to the input of the harvesting circuit on the shepherd cape.
The circuit is a software-controlled and -monitored current-sink with a variable voltage.

By generalizing the approach of shepherd v1 with a dedicated harvest-IC the circuit became more flexible.
The software currently supports to switch between constant voltage (CV) harvesting and maximum power point trackers ([MPPT](https://en.wikipedia.org/wiki/Maximum_Power_Point_Tracking)), with
an open circuit voltage (VOC) or perturb & observe (PO) algorithm.
The implementation is parametrized and can therefore be altered on the fly, e.g. to mimic a BQ25505-Converter by scheduling the 256 ms long VOC measurement every 16 s.

A second advantage of the circuit is that it allows to capture the character of the harvesting transducer as well as the energy scenario.
A harvesting transducer is characterized by its IV-curve, determining the magnitude of current at a specific load voltage.
By capturing a continuous stream of curves the energy scenario is recorded as well.
This abstraction decouples the harvesting from the recording-process and postpones it. The harvesting-algorithm can therefore become part of the emulation-process.

A group of shepherd observers can be deployed to the environment of interest to measure the energy that can be harvested at each node.
The time-synchronization allows to gather the readings from multiple observers with respect to a common time-line.
The data thus represents the spatio-temporal energy availability.

## Emulator

In emulator mode, spatio-temporal current and voltage data is replayed to a group of sensor nodes (targets).
Each shepherd observer hosts a current source that can precisely supply the target ports and regulate in real-time.
Relying on time-synchronization, shepherd can thus faithfully reproduce previously recorded (or model-based) spatio-temporal energy conditions.

The user has the option of adding virtual power-supply parts between the energy-recording (input) and the target port (output), see [](./virtual_source).
This approach can be seen as a hardware-in-the-loop simulation ([HIL](https://en.wikipedia.org/wiki/Hardware-in-the-loop_simulation)) that - similar to the harvester - is fully parametrized.

```{figure} media/virtual_source_schemdraw.png
:name: vsource_schem

fully customizable power supply toolchain
```

The calculations are energy-based and happen in real-time. As default the components behave neutral, so the pictured diodes and resistors have a voltage drop of 0 V, and the central intermediate storage capacitor has no capacity.
This allows to define presets by specifying a minimal parameter-set. Some directly usable presets are:

- direct / neutral
- diode + capacitor
- diode + resistor + capacitor
- BQ25504 (boost only)
- BQ25570 (boost + buck)
- BQ-Converter with an immediate (schmitt-) trigger for power-good-signal (common modification)

In case of recorded IV-Curves there is also the option of specifying the harvest-algorithm.
The parameters will be explained in depth in the chapter [](./virtual_source_old.rst).

Like other testbeds, shepherd records the targets power draw (voltage and current) during emulation.
Furthermore, nine GPIO lines (including bidirectional UART) are level-translated between shepherd and the attached target.
This allows to record and trace the target-behavior.

## Remote programming/debugging

Both target-ports feature four programming lines. These can either be used for two separate SWD- and SBW-connections or in theory for one JTAG-connection to program a variety of MCUs. Shepherds current [nRF52-Target with FRAM](https://github.com/nes-lab/shepherd-targets) makes use of that flexibility by pairing the nRF52 with the MSP430FR.

For convenient debugging and development, shepherd implements a fully functional Serial-Wire-Debug (SWD) debugger, leveraging the power of [OpenOCD](https://openocd.org/).
SWD is supported by most recent ARM Cortex-M and allows flashing images and debugging the execution of code.
Older platforms typically provide a serial bootloader, which can be used to flash images over the pre-mentioned UART connection. The same approach should work for JTAG.

```{note}
The openOCD-method was officially deprecated and deactivated, but with a bit of tinkering it can be installed and used.
```

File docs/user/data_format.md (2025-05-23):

# Data format

Data is stored in the popular [Hierarchical Data Format](https://en.wikipedia.org/wiki/Hierarchical_Data_Format).

This section describes the essential structure of data recorded with shepherd:

```text
    .
    |-- attributes
    |   `-- mode
    |-- data
    |   |-- datatype
    |   |-- window_samples
    |   |-- time
    |   |   `-- attributes
    |   |       |-- gain
    |   |       `-- offset
    |   |-- current
    |   |   `-- attributes
    |   |       |-- gain
    |   |       `-- offset
    |   `-- voltage
    |       `-- attributes
    |           |-- gain
    |           `-- offset
    `-- gpio
        |-- time
        `-- values
```

The `mode` attribute allows to distinguish between data from the `harvester` and `emulator`.

The data group contains the actual IV data and can consist of (datatypes):

- `ivsample`s ⇾ continuous samples
  - directly usable by shepherd as input for virtual source / converter
- `ivcurve`s ⇾ characterizing voltage ramps with a specific step-size
  - directly usable by shepherd as input for a virtual harvester (its output are ivsamples)
  - needs `window_samples` to be set to step count
- `ìsc_voc` ⇾ a sample pair of open circuit voltage and short circuit current widely used to characterize solar-cells
  - needs to be (at least) transformed into ivsurface / curves before usage

While the harvester-algorithms are able to produce all three datatypes, the emulator only outputs `ivsamples`.
The datasets `time`, `current` and `voltage` are raw `uint32` (directly from ADC, when possible) and can be converted to their physical equivalent using the corresponding `gain` and `offset` attributes. For better documentation and automatic processing there are additional attributes attached to the datasets (not shown above):

- `unit` contains the SI unit for the scaling operation
- `description` shows how to apply the scaling, i.e. `system time [s] = value * gain + (offset)`

See [](calibration) for more details.

The gpio group stores the timestamp when a GPIO edge was detected and the corresponding bit mask in values.
For example, assume that all are were low at the beginning of the recording.
At time T, GPIO pin 2 goes high.
The value 0x04 will be stored together with the timestamp T in nanoseconds.

:::{note}
There is more data and metadate, like system logs, included in the files created by the testbed. Check the reference-links below for a deeper dive.
:::

There are numerous tools to work with HDF5 and library bindings for all popular programming languages.

## Usage Examples

We offer the [core-library](https://pypi.org/project/shepherd_core) and complementing CLI-wrapper called [shepherd-data](https://pypi.org/project/shepherd_data). Advantages are:

- automatic validation upon opening a recording
- extraction of iv-data including optional down-sampling
- extraction of system logs
- generate overview of file-content and -structure (meta-data)
- plotting of files
  - specific files or whole directories
  - overviews or even specific parts within a time-window

Here's an example how to plot data recorded with shepherd using bare Python:

```python
import h5py
import matplotlib.pyplot as plt

f, axarr = plt.subplots(1, 2)
with h5py.File("rec.h5", "r") as hf:
    # convert time to seconds
    t_gain = hf["data"]["time"].attrs["gain"]
    t_offset = hf["data"]["time"].attrs["offset"]
    time = hf["data"]["time"][:].astype(float) * t_gain + t_offset
    for i, var in enumerate(["voltage", "current", "time"]):
        gain = hf["data"][var].attrs["gain"]
        offset = hf["data"][var].attrs["offset"]
        values = hf["data"][var][:] * gain + offset
        axarr[i].plot(time, values)

plt.show()
```

## Compression & Beaglebone

The BeagleBone is

- supported are uncompressed, lzf and gzip with level 1 (order of recommendation)
  - lzf seems better-suited due to lower load, or if space isn't a constraint: uncompressed (None as argument)
  - note: lzf seems to cause trouble with some third party hdf5-tools
  - compression is a heavy load for the beaglebone, but it got more performant with recent python-versions
- size-experiment A: 24 h of ramping / sawtooth (data is repetitive with 1 minute ramp)
  - gzip-1: 49'646 MiB ⇾ 588 KiB/s
  - lzf: 106'445 MiB ⇾ 1262 KiB/s
  - uncompressed: 131'928 MiB ⇾ 1564 KiB/s
- cpu-load-experiments (input is 24h sawtooth, python 3.10 with most recent libs as of 2022-04)
  - warning: gpio-traffic and other logging-data can cause lots of load

Evaluating CPU-Load and resulting data-rate for different combinations of compressions:

| type       | cpu_util [%] | data-rate [KiB/s] |
|------------|--------------|-------------------|
| gz1_to_gz1 | 65.59        | 352.0             |
| gz1_to_lzf | 57.37        | 686.0             |
| gz1_to_unc | 53.63        | 1564.0            |
| lzf_to_gz1 | 63.18        | 352.0             |
| lzf_to_lzf | 58.60        | 686.0             |
| lzf_to_unc | 55.75        | 1564.0            |
| unc_to_gz1 | 63.84        | 351.0             |
| unc_to_lzf | 57.28        | 686.0             |
| unc_to_unc | 51.69        | 1564.0            |

Setup:

- 120 s emulation
- run on BeagleBone
- sheep-version: tdb
- ubuntu-version: tbd

## References

- [core/writer.py](https://github.com/nes-lab/shepherd-tools/blob/main/shepherd_core/shepherd_core/writer.py) to see the complete file-structure
- [core/reader.py](https://github.com/nes-lab/shepherd-tools/blob/main/shepherd_core/shepherd_core/reader.py) for file-reading, -validation, -extractions and -conversions
- [data/reader.py](https://github.com/nes-lab/shepherd-tools/blob/main/shepherd_data/shepherd_data/reader.py) for higher functions like resampling, plotting and extracting metadata

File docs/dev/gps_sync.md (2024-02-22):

# GPS-Time-Synchronisation

The goal is to precisely synchronize all Linux system clocks in the network to global time obtained from a GPS receiver.
Note how the following description traverses the clock hierarchy top-down starting with the GPS receiver down to the linux clock on the host node.

## General Structure

The primary node is connected to a u-blox GPS receiver, from which it receives a PPS signal via GPIO and global time via UART if the GPS-Modul has a position-fix.
One kernel module and two services work in tandem to provide a grandmaster clock:

- `pps_gmtimer` (kernel module) timestamps edges on a GPIO pin with respect to an internal hardware timer on the AM335x and feeds the timestamps as a Linux pps device.
- `gpsd` talks to the GPS via a serial interface, parses the protocol and extracts timing information that is fed to the following service (chrony).
- `chrony` combines the global timing information from gpsd and the precise PPS signal from the pps device and synchronizes the Linux system clock to global GPS time.

## Hardware setup

The GPS-capelet (see `hardware/capelets/gps`) is stacked on top of the shepherd cape.

- The PPS signal is connected to Timer4 on pin `P8_7`
- The GPS-Uart is connected over UART2 on pins `P9_21` and `P9_22`
- The currently used gps-chip is the u-blox SAM-M8Q

:::{note}
The capelets were designed for shepherd v1, but are mostly compatible with v2.
:::

## Configuring GNSS module

The u-blox GPS receiver can be configured to optimize its performance. To do this directly from the host node the python script: `ubloxmsg_exchange` was
written (see <https://github.com/kugelbit/ubx-packet-exchange>). The configuration files can be found under `config_files`. To this end the following configurations were set:

- SBAS was disabled for better timing information
- The stationary mode was enabled to get a better percussion and a stable performance
- the GPS- and galileo-satellite-systems were enabled to get a fast and stable fix

In addition, the standard config of the receiver leads to the following behavior:

- If the PPS is not locked, the LED on the capelet will not blink. After the lock is attained, the LED will start blinking at 1 Hz.
- NMEA messages are enabled for the UART link which connects to the BeagleBone.

:::{note}
Recent versions of gpsd include a tool `ubxtool`, allowing convenient configuration of ublox receivers:
 - Poll GNSS config: `ubxtool -p CFG-GNSS`
 - Enable Galileo: `ubxtool -e GALILEO`
 - Enable binary messages: `ubxtool -e BINARY`
 - Disable NMEA messages: `ubxtool -d NMEA`
 - Disable SBAS: `ubxtool -d SBAS`
 - Poll time pulse config: `ubxtool -p CFG-TP5`
:::

## Deploy

Please use the ansible gps-host role.
`ansible-playbook deploy.yml`

## Useful commands

Check if PPS pulses are coming: `cat /sys/class/pps/pps0/assert`
On the primary node check that gpsd and chrony are running:

- `systemctl status gpsd`
- `systemctl status chrony`

gpsd comes with a command line client that display GPS data on the commandline: `cgps`
Familiarize with chrony output:

- `chronyc sources -v`
- `chronyc sourcestats -v`
- `chronyc tracking -v`

### Configuration files

- chrony: `/etc/chrony/chrony.conf`
- gpsd: `/etc/default/gpsd`
- the device tree file (dts) for the GPS-caplet is found in the pps-gmtimer folder (DD-GPS-00A0.dts).

### DEBUG

If you want to see what's going on you can run the services in DEBUG-Mode:

- chrony: `sudo chronyd -dd`
- gpsd: `sudo gpsd -N /dev/ttyO2 -D15 -n`

## Pitfalls

- For a good result (fast and stable fixes) it is import to provide a clear sky view to the gps-caplet.
- There are lots of possible configuration options for the u-blox chip (see SAM-M8Q Receiver Description) that may further optimize performance. For more research in this direction use the u-blox u-center software.
- The currently used u-blox chip does not support the u-blox time mode. This mode can increase the timing accuracy (see u-blox M8 Receiver Description).

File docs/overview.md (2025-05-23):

# Overview

This is the main entry point into the shepherd ecosystem. Based on your experience, you might skip the first steps:

1. To learn how *shepherd* enables research into the most challenging problems of coordinating battery-less sensor nodes, take a look at our [paper](https://wwwpub.zih.tu-dresden.de/~mzimmerl/pubs/geissdoerfer19shepherd.pdf).
2. To get a basic understanding of what shepherd does, start with the [](user/basics).
3. If you have the hardware on your desk and want to get started, read [](user/getting_started).
4. To record/emulate data on a group of shepherd nodes, use the [](tools/herd) command line utility.
5. To access the testbed-instance go to <https://nes-lab.github.io/shepherd-nova>.
6. If you'd like to contribute or have issues, try the [](dev/contributing)-guide or jump to the [](user/help_me_help_you)-section.
7. The in-depth DevLog-Documentation is located in: <https://orgua.github.io/shepherd-v2-planning/>

:::{note}
The included search-function is often able to find the needle in the haystack (especially in the overwhelming dev-log)
:::

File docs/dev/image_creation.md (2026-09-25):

# Create a Shepherd-ISO

## Prereqs

- download image (Debian 12 recommended), see [](../user/getting_started.md)
- write to micro-SD card (i.e. with balena etcher)
- activate flasher in `/boot/uEnv.txt`
  - recommended as pulling and writing the final image is much faster (4 GiB vs 32 GiB at ~15 MiB/s)
- have a Beaglebone ready & connected to a network
- insert SD-Card and boot Beaglebone -> image will be copied to internal eMMC -> Larson-Scanner shuts down when done
- test the code
- it helps to have a second micro-SD card ready when it's time to pull an image from the eMMC
- to test the image you need a third SD-card

## Switch Cape-Version

For ansible setup:

- ansible `roles/sheep/defaults/main.yml` has hardcoded `sheep_cape_hw_ver`

For an active installation:

- change device-tree loaded during boot in `/boot/uEnv.txt` (24A0 or 25A0) -> needs reboot
- modify envVar in `./software/build_pru.sh` (24 or 25) and run script to update pru-firmwares
- python pulls cape-version from EEPROM automatically or defaults to the newest version

Check with:

```shell
shepherd-herd shell "sudo cat /boot/uEnv.txt | grep BB-SHEPHERD-CAPE-"
shepherd-herd shell "sudo shepherd-sheep eeprom read --hw-version"
shepherd-herd shell "sudo shepherd-sheep -v version"
```

## Custom Install

- adapt your herd.yaml to point to the one beaglebone, activate roles for sheep and ptp-client
- run ansible `deploy/bootstrap.yml`
- run ansible `deploy/deploy.yml`
- distribute ssh keys of server & admin (`NESLAB/2026-misc/authorized_keys`)
- run ansible `deploy/dev_acquire_image.yml`
- pull image with command given by `deploy/dev_acquire_image.yml`
  - best is to boot from a second SD-Card that was just bootstrapped to avoid data-corruption
- burn image to SD and check if it boots properly

useful commands

```shell
cat /etc/debian_version
# ⤷ currently shows debian 12.15
sudo /usr/sbin/ntpdate -b -s -u pool.ntp.org
# ⤷ for manual timesync
sudo systemctl status phc2sys@eth0
sudo systemctl status ptp4l@eth0
# ⤷ for stopping / starting sync systems
ip a
# ⤷ determine current IP
```

## Distribution to other nodes

- burn image to other SD-cards
- activate sysrqd
- ansible `deploy/setup_testbed_observer.yml` (secure, MAC broadcasting, NFS mounting)
- grow partition? -> add to observer-role?

Update distro

```Shell
shepherd-herd shell "sudo apt update"
shepherd-herd shell "sudo apt dist-upgrade -y"
```

Activate [SysRqd](https://github.com/jd/sysrqd)

```Shell
shepherd-herd shell "sudo apt install sysrqd -y"
shepherd-herd shell "echo 'YOUR_COMPLEX_CUSTOM_PASSWORD' > ~/sysrqd.secret"
shepherd-herd shell "sudo mv ~/sysrqd.secret /etc/"
shepherd-herd shell "sudo chmod 0600 /etc/sysrqd.secret"

shepherd-herd shell "sudo systemctl restart sysrqd"
shepherd-herd shell "sudo systemctl status sysrqd"

# optional test:
telnet 192.168.165.200 4094
# -> only working inside sheep-network (also from web-server)
> PW
> b  (for hard reboot)
# to exit: ctrl + altgr + ] -> on telnet-console: quit
```

Activate Internet-Watchdog by copying / modifying config (BETA):

```Shell
# on local observer
sudo nano /etc/shepherd/watchdog.yaml
# set
#   network_needed: true
```

Grow Main-Partition on SD

```shell
shepherd-herd shell "yes | sudo parted /dev/mmcblk0 resizepart 1 100% ---pretend-input-tty"
shepherd-herd shell "sudo resize2fs /dev/mmcblk0p1"
shepherd-herd shell "df -h | grep mmc"
```

Add local shepherd-repo

```shell
shepherd-herd shell "sudo rm -rf /opt/shepherd"
shepherd-herd shell "cd /opt/ && sudo git clone https://github.com/nes-lab/shepherd"
shepherd-herd shell "sudo chown -R jane /opt/shepherd/"
shepherd-herd shell "sudo chmod a+rwx -R /opt/shepherd/"
#shepherd-herd shell "cd /opt/shepherd && git checkout dev"
shepherd-herd shell "cd /opt/shepherd && git pull"
```

In your local shepherd-repo you can add the observer-role to the nodes:

```Shell
ansible-playbook deploy/setup_testbed_observer.yml
```

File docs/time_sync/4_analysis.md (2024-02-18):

# Analysis

## Prepare Data

- Logic 2 Software -> File -> Export Data
- select channels: 1-3
- Time Range: All Time
- Format: CSV
- DON'T use ISO8601 timestamps
- Export and rename file to meaningful description

logic_export

## Exemplary Analysis

Comparison between three embedded platforms and their performance

### Setup

- same cisco switch
- same software configuration (where possible)
- data recorded with a Logic Pro 16 @ 500 MHz
- nodes & network are at rest (baseline)

### GPIO - Jitter

How accurate is the 100 ms trigger on different platforms? Let's visualize the jitter of one node.

In numbers:
- simplified
- `Δ_q1 = 99%-Quantile - 1%-Quantile`
- `Δ_max = Max - Min`

| name                              | Δ_q1 [ns] | Δ_max [ns] |
|-----------------------------------|-----------|------------|
| BBB_023_ABS_HARD_ch0_rising_100ms | 874       | 1050       |
| BBAI_02_ptp_piservo_[..]ing_100ms | 464       | 16552      |
| 010_cm4_baseline_ch0_rising_100ms | 78        | 286        |

**BBone Black**

GPIO-Jitter-BBB

**BBone AI64**

GPIO-Jitter-BBAI

**Raspberry Pi CM4**

GPIO-Jitter-RPiCM4

#### Some context and final words:

- BBB takes ~ 300 ns to get kernel time. performance looks fine considering the age of the platform
- BBAI takes ~ 40 ns to get kernel time. the random spikes are still unexplained. It could be caused by register-write-locks. The SOC has several coprocessors that share the same bus (linux shows 2ß rProc). Also the system is missing a RT-Kernel.
- CM4 was overclocked to match BB-Ai, so it also takes ~ 40 ns to get kernel time. jitter looks best of these three systems

### Sync Performance

In numbers:
- `Δ_q1 = 99%-Quantile - 1%-Quantile`
- `Δ_max = Max - Min`

| name                         | Δ_q1 [ns] | Δ_max [ns] |
|------------------------------|-----------|------------|
| BBAI_02_ptp_piservo_[..]_1u2 | 669       | 1182       |
| RPI_005_norm_80_70_diff_1u2  | 336       | 378        |

**BBone AI64**

Sync-BBAI

**Raspberry Pi CM4**

Sync-RPiCM4

### Deeper Dive

Raw data and Plots are at [shepherd-planning](https://github.com/orgua/shepherd_v2_planning/tree/main/timesync'24)

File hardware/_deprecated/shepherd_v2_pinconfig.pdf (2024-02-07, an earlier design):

PinHeader | GPIO | Name | BB_Blocked PRU | ShepV1-FN | GPS-Capelet | nRF52 | ShepV2-FN | copy-pin
P8_07 | | 66 TIMER4 | | xxx | GPS_PPS | | (GPS) | P8_07
P8_08 | | 67 TIMER7 | | xxx | GPS_nRESET | | (GPS) | P8_08
P8_09 | 69 TIMER5 | xxx | GPS_nSAFEBOOT | (GPS) | P8_09
P8_10 | | 68 TIMER6 | | | | | WD_ACK | P8_10
P8_11 | 45 | pr1_pru0_pru_r30_15 Debug Pin0 PRU0 | pru0_dbg_Led1 | P8_11
P8_12 | 44 | pr1_pru0_pru_r30_14 Led1 PRU0 | pru0_dbg_Led0 | P8_12
P8_13 | 23 | EN Harvester | EN_Shepherd | P8_13
P8_14 | 26 | target_GPIO0 | P8_14
P8_15 | 47 | pr1_pru0_pru_r31_15 | target_GPIO3 | P8_15
P8_16 | 46 | pr1_pru0_pru_r31_14 | target_GPIO2 | P8_16
P8_17 | 27 | target_GPIO1 | P8_17
P8_18 | 65 | BTN Sense | P8_18
P8_19 | | 22 EHRPWM2A | | | | | BTN Led | P8_19
P8_26 | 61 | target_GPIO4 | P8_26
P8_27 | 86 | HDMI | pr1_pru1_pru_r31_08 | pru1_target_batOK | P8_27
P8_28 | 88 | HDMI | pr1_pru1_pru_r31_10 | ADC RST / PDN | pru1_dbg_Led0 | P8_28
P8_29 | 87 | HDMI | pr1_pru1_pru_r31_09 | pru1_target_GPIO4 | P8_29
P8_30 | 89 | HDMI | pr1_pru1_pru_r31_11 | Led2 User Space | pru1_dbg_Led1 | P8_30
P8_39 | 76 | HDMI | pr1_pru1_pru_r31_06 | pru1_target_swd_clk P8_39
P8_40 | 77 | HDMI | pr1_pru1_pru_r31_07 | pru1_target_swd_io P8_40
P8_41 | 74 | HDMI | pr1_pru1_pru_r31_04 Debug Pin0 PRU1 | pru1_target_uatx | P8_41
P8_42 | 75 | HDMI | pr1_pru1_pru_r31_05 Debug Pin1 PRU1 | pru1_target_uarx | P8_42
P8_43 | 72 | HDMI | pr1_pru1_pru_r31_02 Target GPIO2 | GPIO2 | pru1_target_GPIO2 | P8_43
P8_44 | 73 | HDMI | pr1_pru1_pru_r31_03 | Target GPIO3 | GPIO3 | pru1_target_GPIO3 | P8_44
P8_45 | 70 | HDMI | pr1_pru1_pru_r31_00 Target GPIO0 | GPIO0 | pru1_target_GPIO0 | P8_45
P8_46 | 71 | HDMI | pr1_pru1_pru_r31_01 | Target GPIO1 | GPIO1 | pru1_target_GPIO1 | P8_46
P9_11 | | 30 UART4_RXD | | EN MPPT | | | target_io_SEL | P9_11
P9_12 | 60 | EN V Analog | target_io_EN | P9_12
P9_13 | | 31 UART4_TXD | | | | | target_Pwr_SEL | P9_13
P9_17 | | 5 I2C1_SCL | | I2C1_SCL | | | target_swd_clk | P9_17
P9_18 | | 4 I2C1_SDA | | I2C1_SDA | | | target_swd_io | P9_18
P9_19 | | 13 I2C2_SCL | I2C | I2C2_SCL | | | Mem_SCL | P9_19
P9_20 | | 12 I2C2_SDA | I2C | I2C2_SDA | | | Mem_SDA | P9_20
P9_21 | | 3 UART2_TXD | | xxx | UART2_TX | | (GPS_UART) | P9_21
P9_22 | | 2 UART2_RXD | | xxx | UART2_RX | | (GPS_UART) | P9_22
P9_23 | 49 | Mem_WP | P9_23
P9_24 | | 15 UART1_TXD | pr1_pru0_pru_r31_16 | UART_TX | | UART_TX | target_uart_tx | P9_24
P9_25 | 117 | mcasp | pr1_pru0_pru_r31_07 | SPI CS ADC | pru/SPI_CS_ADC2_REC P9_25
P9_26 | 14 UART1_RXD | pr1_pru1_pru_r31_16 UART_RX | UART_RX | target_uart_rx | P9_26
P9_27 | 115 | mcasp | pr1_pru0_pru_r31_05 | SPI MISO | pru/SPI_CS_DAC_REC P9_27
P9_28 | 113 SPI1_CS0 | mcasp | pr1_pru0_pru_r31_03 SPI SCLK | pru/SPI_CS_DAC_EMU P9_28
P9_29 | 111 SPI1_DO | mcasp | pr1_pru0_pru_r31_01 | Select LOAD PRU | pru/SPI_MOSI | P9_29
P9_30 | 112 SPI1_D1 | mcasp | pr1_pru0_pru_r31_02 SPI MOSI | pru/SPI_MISO | P9_30
P9_31 | 110 SPI1_SCLK | mcasp | pr1_pru0_pru_r31_00 | SPI CS DAC | pru/SPI_SCK | P9_31
P9_41A | | 20 CLKOUT2 | | SWDIO | | SWDIO | (shared pin) | P9_41A
P9_41B | 116 | pr1_pru0_pru_r31_06 | pru/SPI_CS_ADC1_REC P9_41B
P9_42A | | 7 SPI1_CS1 | mcasp | SWDCLK | | SWDCLK | (shared pin) | P9_42A
P9_42B | 114 | mcasp | pr1_pru0_pru_r31_04 | pru/SPI_CS_ADC_EMU P9_42B

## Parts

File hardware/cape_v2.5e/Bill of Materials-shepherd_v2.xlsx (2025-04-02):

Comment | Designator | Footprint | LibRef | Quantity | Manufacturer | Manufacturer PN | Distributer | Distributer PN | Price n10 [€]
C_0402_1nF_50V_NP0 | C1, C3, C32, C133, C141, C155, C157 | CAPC1005X06 | .C_0402_1nF_50V | 7 | Murata | GRM1555C1H102JA01D | Mouser | 81-GRM1555C1H102JA1D | 0.02
C_0402_100nF_25V_X7R | C2, C4, C11, C12, C14, C20, C22, C34, C35, C38, C39, C40, C41, C71, C78, C79, C80, C84, C85, C86, C91, C98, C105, C108, C118, C120, C122, C123, C124, C125, C126, C127, C128, C129, C136, C144, C156 | CAPC1005X06 | .C_0402_100nF_25V | 37 | Murata | GRM155R71E104KE14J | Mouser | 81-GRM155R71E104KE4J | 0.025
C_0402_1uF_10V_X7R | C5, C7, C10, C13, C17, C18, C21, C23, C24, C31, C33, C36, C42, C43, C44, C45, C46, C49, C64, C65, C68, C69, C81, C100, C106, C119, C121, C130, C131, C132, C134, C135, C137, C138, C139, C149 | CAPC1005X06 | .C_0402_1uF_X7R_10V | 36 | Murata | GRM155C71A105KE11D | Mouser | 81-GRM155C71A105KE1D | 0.036
C_0402_10nF_25V_NP0 | C6, C30, C62, C93, C96 | CAPC1005X06 | .C_0402_10nF_25V_NP0 | 5 | Murata | GRM1555C1E103JE01J | Mouser | 81-GRM1555C1E103JE1J | 0.15
C_0603_10uF_16V_X5R | C8, C9, C16, C19, C25, C26, C28, C29, C48, C76, C77, C87, C90, C92, C94, C95, C97, C103, C107, C109, C111, C115, C117, C154 | CAPC1608X09 | .C_0603_10uF_16V | 24 | Taiyo Yuden | EMK107BBJ106MA-T | Mouser | 963-EMK107BBJ106MA-T | 0.14
C_1206_100uF_6V3_X5R | C15, C27, C88, C101, C102, C145 | CAPC3216X18 | .C_1206_100uF_6V3 | 6 | Taiyo Yuden | JMK316ABJ107ML-T | Mouser | 963-JMK316ABJ107ML-T | 0.25
C_1206_47uF_16V_X5R | C47, C162 | CAPC3216X18 | .C_1206_47uF_16V | 2 | Taiyo Yuden | EMK316BBJ476ML-T | Mouser | 963-EMK316BBJ476ML-T | 0.34
C_1206_47uF_10V_X5R | C82, C83, C110, C112, C114, C116, C146 | CAPC3216X18 | .C_1206_47uF_10V | 7 | Taiyo Yuden | LMK316ABJ476ML-T | Mouser | 963-LMK316ABJ476ML-T | 0.23
C_0402_47pF_50V_NP0 | C104 | CAPC1005X06 | .C_0402_47pF_50V | 1 | Kemet | C0402C470K5GACTU | Mouser | 80-C0402C470K5G | 0.01
C_0402_10uF_4V_X6S | C147, C148 | CAPC1005X06 | .C_0402_10uF_X6S_4V | 2 | Murata | GRM155C80G106ME44D | Mouser | 81-GRM155C80G106ME44 | 0.04
C_1206_220uF_6V3_X5R | C150, C151, C152, C160, C161 | CAPC3216X18 | .C_1206_220uF_6V3 | 5 | Murata | GRM31CR60J227ME11K | Mouser | 81-GRM31CR60J227ME1K | 0.56
D_LED_0603_Amber | D3, D4, D5, D6 | DIOM1608X02N Orange | .D_LED_0603_Amber | 4 | Wuerth | 150060AS75000 | Mouser | 710-150060AS75000 | 0.12
D_LED_0603_Green | D7, D8, D13, D16, D17 | DIOM1608X02N Green | .D_LED_0603_Green | 5 | Wuerth | 150060VS55040 | Mouser | 710-150060VS55040 | 0.14
NSR05T30XV2 | D10, D11, D12, D14 | SODFL160X70-2N | .D_SOD523_370mV_500mA | 4 | On Semi | NSR05T30XV2T5G | Mouser | 863-NSR05T30XV2T5G | 0.18
J_T1x2_3.5mm_Screw | J1 | P_Phoenix_1984617 | .J_T1x2_3.5mm_Screw | 1 | Phoenix Contact | 1984617 | Mouser | 651-1984617 | 0.39
L_FB_0603_Z600R_1300mA | L1, L2 | INDC1608X08 | .L_FB_0603_Z600R_1300mA | 2 | Murata | BLM18KG601SN1D | Mouser | 81-BLM18KG601SN1D | 0.05
L_NR3015T1R5M | L3 | INDP3030X15N | .L_NR3015T1R5M | 1 | Taiyo Yuden | NR3015T1R5N | Mouser | 963-NR3015T1R5N | 0.20
L_SRN4026-2R2Y | L4 | INDP4040X25N | .L_SRN4026-2R2Y | 1 | Bourns | SRN4026-2R2Y | Mouser | 652-SRN4026-2R2Y | 0.38
L_NR3015T150M | L5, L8, L9, L12 | INDP3030X15N | .L_NR3015T150M | 4 | Taiyo Yuden | NR3015T150M | Mouser | 963-NR3015T150M | 0.23
SMS-455Cover | M1 |  | SMS-455Cover | 1 | LeaderTech | SMS-455-N-C | Mouser | 861-SMS-455-N-C | 0.34
SMS-455Frame | M2 | SMS-455F-wPaste | SMS-455Frame | 1 | LeaderTech | SMS-455-N-F | Mouser | 861-SMS-455-N-F | 1.87
BeagleBoneGreen | P1 |  | BeagleBoneGreen | 1 | Seeed Studio | 102010027 | RS-Online | 174-3279 | 39.19
P_JST_S4B_ZR-SM4A | P2 | P_JST_S4B-ZR-SM4A | .P_JST_S4B_ZR-SM4A | 1 | JST | S4B-ZR-SM4A-TF(LF)(SN) | Digikey | 455-1695-1-ND | 0.51
P_HDR_2x5_2.00mm | P3 | P_Pinheader_2x5_R2.0mm | .P_HDR_2x5_2.00mm | 1 |  |  | Mouser
Beaglebone P8 | P8 | P_Pinheader_2x23_R2.54mm_LongPinHeader | Beaglebone P8 | 1 | Samtec | SSQ-123-03-G-D | Digikey | SAM1196-23-ND | 6.45
Beaglebone P9 | P9 | P_Pinheader_2x23_R2.54mm_LongPinHeader | Beaglebone P9 | 1 | Samtec | SSQ-123-03-G-D | Digikey | SAM1196-23-ND | 6.45
P_HSEC8-120-01-S-DV | P10, P11 | P_HSEC8-120-01-S-DV | .P_HSEC8-120-01-S-DV | 2 | Samtec | HSEC8-120-01-L-DV-A-K-TR | Mouser | 200-HSEC812001LDVAKT | 3.17
R_0402_1k | R1, R3, R5, R8, R16, R18, R21, R56, R57, R58, R59, R60, R61, R62, R63, R64, R65, R66, R67, R68, R70, R79, R80, R82, R83, R84, R91, R92, R93, R94, R107, R112, R113, R124, R125, R126, R127, R133, R134 | RESC1005X04 | .R_0402_1k | 39 | Panasonic | ERJ-2GEJ102X | Mouser | 667-ERJ-2GEJ102X | 0.02
R_0402_2R | R2 | RESC1005X04 | .R_0402_2R | 1 | Panasonic | ERJ-2GEJ2R0X | Mouser | 667-ERJ-2GEJ2R0X | 0.02
R_0402_10k | R4, R6, R7, R11, R87, R88, R89, R90, R95, R96, R97, R102, R103 | RESC1005X04 | .R_0402_10k | 13 | Yageo | RC0402FR-7W10KL | Mouser | 603-RC0402FR-7W10KL | 0.01
R_1206_2R_0.25% | R9 | RESC3116X06 Shunt | .R_1206_2R_0.25% | 1 | Yageo | RT1206CRD072RL | Mouser | 603-RT1206CRD072RL | 0.35
R_0402_33R | R10, R22, R23, R69, R71, R72, R74, R75, R76, R77, R78, R81, R85, R86 | RESC1005X04 | .R_0402_33R | 14 | Panasonic | ERJ-2GEJ330X | Mouser | 667-ERJ-2GEJ330X | 0.02
R_0402_210R_0.1% | R12, R130 | RESC1005X04 | .R_0402_210R_0.1% | 2 | Yageo | RT0402BRD07210RL | Mouser | 603-RT0402BRD07210RL | 0.19
R_0603_DNP | R13 | RESC1608X06N-DNP | .R_0603_DNP | 1 |  |  | Mouser
R_0402_470R | R14, R100, R106, R109 | RESC1005X04 | .R_0402_470R_1% | 4 | Panasonic | ERJ-2RKF4700X | Mouser | 667-ERJ-2RKF4700X | 0.028
R_0402_5k1_1% | R15 | RESC1005X04 | .R_0402_5k1_1% | 1 | Yageo | RC0402FR-075K1L | Mouser | 603-RC0402FR-075K1L | 0.008
R_0402_100k_1% | R17, R19, R20, R25, R27, R29, R30, R31, R32, R33, R34, R35, R36, R37, R38, R40, R42, R43, R44, R45, R46, R47, R48, R49, R50, R52, R54, R98, R101, R105, R111, R128 | RESC1005X04 | .R_0402_100k | 32 | Panasonic | ERJ-2RKF1003X | Mouser | 667-ERJ-2RKF1003X | 0.02
R_0402_240R | R24, R26, R28, R39, R41, R51, R53, R55, R114, R115, R116, R117, R118, R119, R120, R121, R122, R123 | RESC1005X04 | .R_0402_240R | 18 | Panasonic | ERJ-2GEJ241X | Mouser | 667-ERJ-2GEJ241X | 0.02
R_0402_10R | R73, R129 | RESC1005X04 | .R_0402_10R | 2 | Panasonic | ERJ-2GEJ100X | Mouser | 667-ERJ-2GEJ100X | 0.02
R_0402_24k | R99 | RESC1005X04 | .R_0402_24k | 1 | Panasonic | ERJ-2GEJ243X | Mouser | 667-ERJ-2GEJ243X | 0.02
R_0402_680k_1% | R104 | RESC1005X04 | .R_0402_680k_1% | 1 | Panasonic | ERJ-2RKF6803X | Mouser | 667-ERJ-2RKF6803X | 0.02
R_0402_240k_1% | R108, R110 | RESC1005X04 | .R_0402_240k_1% | 2 | Panasonic | ERJ-2RKF2403X | Mouser | 667-ERJ-2RKF2403X | 0.02
R_0402_100R | R131, R132 | RESC1005X04 | .R_0402_100R | 2 | Panasonic | ERJ-2GEJ101X | Mouser | 667-ERJ-2GEJ101X | 0.02
BSH105 | T1, T2 | SOT95P230X110-3N | .T_BSH105 | 2 | Nexperia | BSH105,215 | Mouser | 771-BSH105215 | 0.21
OPA2388 | U1 | TSOP65P490X110-8N | OPA2388 | 1 | TI | OPA2388IDGKR | Mouser | 595-OPA2388IDGKR | 2.63
UA_DAC8562-DSC | U2 | PSON50P300X80_HS-11N | DAC8562-DSC | 1 | TI | DAC8562SDSCR | Mouser | 595-DAC8562SDSCR | 6.73
AD8421B | U3 | TSOP65P490X110-8N | AD8421B | 1 | Analog | AD8421BRMZ | Mouser | 584-AD8421BRMZ | 8.10
ADS8691 | U4 | TSOP65P640X120-16N | ADS8691 | 1 | TI | ADS8691IPWR | Mouser | 595-ADS8691IPWR | 8.5
UP_TPS62913 | U5 | VQFN50P200X200X100_HS-10N | TPS62913 | 1 | TI | TPS62913RPUR | Mouser | 595-TPS62913RPUR | 2.90
UD_74LVC2T45-GT | U6, U7, U11, U12, U23, U24, U25, U26, U27, U28, U29 | SON50P100X50_HS-9N | 74LVC2T45GT | 11 | Nexperia | 74LVC2T45GT,115 | Mouser | 771-74LVC2T45GT115 | 0.37
UD_PI5A4157ZU | U8, U9, U16, U34, U36, U37, U38, U39, U40, U41, U42, U43, U44, U45, U46, U47, U48, U49 | SON35P100X60-6N | PI5A4157ZU | 18 | Diodes Inc | PI5A4157ZUEX | Mouser | 729-PI5A4157ZUEX | 0.54
UA_OPA388-DBV | U10, U32 | SOT95P280X145-5N | OPA388-DBV | 2 | TI | OPA388IDBVR | Mouser | 595-OPA388IDBVR | 1.80
UD_NLAS4684-MN | U13, U33, U35 | PSON50P300X100_HS-11N | NLAS4684-MN | 3 | ON Semi | NLAS4684MNR2G | Mouser | 863-NLAS4684MNR2G | 0.63
TC7WH08FK | U14 | TSSOP50P310X80-8N | TC7WH08FK | 1 | Toshiba | TC7WH08FK,LJ(CT | Mouser | 757-TC7WH08FKLJCT | 0.24
HCT2G04 | U15 | SOT65P210X110-6N | HCT2G04 | 1 | Nexperia | 74HC2G04GW,125 | Mouser | 771-HC2G04GW125 | 0.21
UD_CAT24C256-HU | U17 | PSON50P300X55_HS-9N | CAT24C256-HU4 | 1 | ON Semi | CAT24C256HU4IGT3 | Mouser | 863-CAT24C256HU4IGT3 | 0.36
TPL5010 | U18 | SOT95P280X100-6N | TPL5010 | 1 | TI | TPL5010DDCR | Mouser | 595-TPL5010DDCR | 0.62
LP2989-5.0 | U19 | TSOP65P490X110-8N | LP2989-5.0 | 1 | TI | LP2989AIMM-5.0/NOPB | Mouser | 926-LP2989AIMM50NOPB | 2.05
MP3221 | U20 | SOT95P280X100-6N | MP3221 | 1 | MPS | MP3221GJ-Z | Mouser | 946-MP3221GJ-Z | 1.33
LP2989-3.3 | U21 | TSOP65P490X110-8N | LP2989-3.3 | 1 | TI | LP2989AIMM-3.3/NOPB | Mouser | 926-LP2989AIMM33NOPB | 3.47
LT3487 | U22 | PSON50P300X100_HS-11N | LT3487 | 1 | Analog | LT3487EDD#TRPBF | Mouser | 584-LT3487EDD#TRPBF | 2.72
UD_74HC4066-BQ | U30, U31 | PQFN50P250X300X100_HS-15N | 74HC4066BQ | 2 | Nexperia | 74HC4066BQ,115 | Mouser | 771-HC4066BQ115 | 0.27

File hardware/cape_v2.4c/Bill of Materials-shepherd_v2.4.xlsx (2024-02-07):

Comment | Designator | Footprint | LibRef | Quantity | Manufacturer | Manufacturer PN | Distributer | Distributer PN | Price n10 [€]
C_0402_1nF_50V | C1, C3, C28, C29, C34, C36, C73, C133, C141, C143, C147 | CAPC1005X06 | .C_0402_1nF_50V | 11 | Murata | GRM1555C1H102JA01D | Mouser | 81-GRM1555C1H102JA1D | 0.02
C_0402_100nF_25V | C2, C4, C11, C12, C14, C20, C22, C27, C30, C37, C43, C46, C52, C54, C56, C58, C60, C63, C66, C67, C70, C71, C74, C78, C79, C80, C84, C85, C86, C91, C98, C105, C108, C113, C118, C120, C122, C123, C124, C125, C126, C127, C128, C129, C136, C144, C155, C156 | CAPC1005X06 | .C_0402_100nF_25V | 48 | Murata | GRM155R71E104KE14J | Mouser | 81-GRM155R71E104KE4J | 0.025
C_0402_1uF_10V_X7R | C5, C7, C10, C13, C17, C18, C21, C23, C31, C38, C39, C42, C45, C49, C50, C53, C55, C57, C59, C61, C64, C65, C68, C69, C72, C75, C81, C99, C100, C106, C119, C121, C130, C131, C132, C134, C135, C137, C138, C139, C148, C149 | CAPC1005X06 | .C_0402_1uF_X7R_10V | 42 | Murata | GCM155C71A105KE38D | Mouser | 81-GCM155C71A105KE8D | 0.05
C_0402_10nF_25V_NP0 | C6, C35, C62, C93, C96, C140, C142 | CAPC1005X06 | .C_0402_10nF_25V_NP0 | 7 | Murata | GRM1555C1E103JE01J | Mouser | 81-GRM1555C1E103JE1J | 0.15
C_0603_10uF_16V | C8, C9, C15, C16, C19, C24, C25, C26, C32, C33, C40, C41, C44, C48, C51, C76, C77, C87, C90, C92, C94, C95, C97, C103, C107, C109, C111, C115, C117, C153, C154 | CAPC1608X09 | .C_0603_10uF_16V | 31 | Taiyo Yuden | EMK107BBJ106MA-T | Mouser | 963-EMK107BBJ106MA-T | 0.14
C_D8L12_470uF_25V | C47 | CAP-ELCO_D8L12mm | .C_D8L12_470uF_25V | 1 | Wurth | 860020474014 | Mouser | 710-860020474014 | 0.25
C_1206_47uF_10V | C82, C83, C110, C112, C114, C116, C146 | CAPC3216X18 | .C_1206_47uF_10V | 7 | Taiyo Yuden | LMK316ABJ476ML-T | Mouser | 963-LMK316ABJ476ML-T | 0.23
C_1206_100uF_6V3 | C88, C89, C101, C102, C145 | CAPC3216X18 | .C_1206_100uF_6V3 | 5 | Taiyo Yuden | JMK316ABJ107ML-T | Mouser | 963-JMK316ABJ107ML-T | 0.25
C_0402_47pF_50V | C104 | CAPC1005X06 | .C_0402_47pF_50V | 1 | Kemet | C0402C470K5GACTU | Mouser | 80-C0402C470K5G | 0.01
C_D8L12_680uF_10V | C150 | CAP-ELCO_D8L12mm | .C_D8L12_680uF_10V | 1 | Wurth | 860020274013 | Mouser | 710-860020274013 | 0.20
C_D8L12_1mF_6V3 | C151, C152 | CAP-ELCO_D8L12mm | .C_D8L12_1mF_6V3 | 2 | Nichicon | UVR0J102MPD1TD | Mouser | 647-UVR0J102MPD1TD | 0.25
D_SOD123W_710mV_1A | D1 | SODFL350X110-2N | .D_SOD123W_710mV_1A | 1 | Nexperia | PMEG10010ELRX | Mouser | 771-PMEG10010ELRX | 0.24
D_LED_0603_Amber | D3, D4, D5, D6 | DIOM1608X02N Orange | .D_LED_0603_Amber | 4 | Wuerth | 150060AS75000 | Mouser | 710-150060AS75000 | 0.12
D_LED_0603_Green | D7, D8, D13, D16, D17 | DIOM1608X02N Green | .D_LED_0603_Green | 5 | Wuerth | 150060VS55040 | Mouser | 710-150060VS55040 | 0.14
D_SOD523_370mV_500mA | D10, D11, D12, D14 | SODFL160X70-2N | .D_SOD523_370mV_500mA | 4 | On Semi | NSR05T30XV2T5G | Mouser | 863-NSR05T30XV2T5G | 0.18
J_T1x2_3.5mm_Screw | J1 | P_Phoenix_1984617 | .J_T1x2_3.5mm_Screw | 1 | Phoenix Contact | 1984617 | Mouser | 651-1984617 | 0.39
L_FB_0603_Z600R_1300mA | L1, L2 | INDC1608X08 | .L_FB_0603_Z600R_1300mA | 2 | Murata | BLM18KG601SN1D | Mouser | 81-BLM18KG601SN1D | 0.05
L_NR3015T1R5M | L3 | INDP3030X15N | .L_NR3015T1R5M | 1 | Taiyo Yuden | NR3015T1R5N | Mouser | 963-NR3015T1R5N | 0.20
L_NR3015T150M | L5, L8, L9, L12 | INDP3030X15N | .L_NR3015T150M | 4 | Taiyo Yuden | NR3015T150M | Mouser | 963-NR3015T150M | 0.23
SMS-455Cover | M1, M3 |  | SMS-455Cover | 2 | LeaderTech | SMS-455-N-C | Mouser | 861-SMS-455-N-C | 0.34
SMS-455FrameOpen | M2 | SMS-455F - Neighbour | SMS-455FrameOpen | 1 | LeaderTech | SMS-455-N-F | Mouser | 861-SMS-455-N-F | 1.87
SMS-455Frame | M4 | SMS-455F | SMS-455Frame | 1 | LeaderTech | SMS-455-N-F | Mouser | 861-SMS-455-N-F | 1.87
BeagleBoneGreen | P1 |  | BeagleBoneGreen | 1 | Seeed Studio | 102010027 | RS-Online | 174-3279 | 39.19
P_JST_S4B_ZR-SM4A | P2 | P_JST_S4B-ZR-SM4A | .P_JST_S4B_ZR-SM4A | 1 | JST | S4B-ZR-SM4A-TF(LF)(SN) | Digikey | 455-1695-1-ND | 0.51
P_GCT_USB4125_GFA | P3 | P_GCT_USB4125-GF-A | .P_GCT_USB4125_GFA | 1 | GCT | USB4125-GF-A | Mouser | 640-USB4125-GF-A | 0.43
P_HDR_2x2_2.54mm_header | P6 | P_Pinheader_2x2_R2.54mm | .P_HDR_2x2_2.54mm_male | 1 | Amphenol | 861400042YO2319LF | Mouser | 649-86140042YO2319LF | 0.12
Beaglebone P8 | P8 | P_Pinheader_2x23_R2.54mm_LongPinHeader | Beaglebone P8 | 1 | Samtec | SSQ-123-03-G-D | Digikey | SAM1196-23-ND | 6.45
Beaglebone P9 | P9 | P_Pinheader_2x23_R2.54mm_LongPinHeader | Beaglebone P9 | 1 | Samtec | SSQ-123-03-G-D | Digikey | SAM1196-23-ND | 6.45
P_HDR_2x9_2.54mm_header | P10, P11 | P_Pinheader_2x9_R2.54mm_male | .P_HDR_2x9_2.54mm_male | 2 | Amphenol FCI | 10129381-918001BLF | Mouser | 649-1012938191801BLF | 0.28
R_0402_1k | R1, R3, R5, R8, R14, R15, R18, R24, R27, R55, R56, R57, R59, R60, R61, R62, R63, R64, R65, R66, R67, R68, R79, R80, R82, R83, R91, R92, R93, R94, R112, R113, R124, R125, R126, R127 | RESC1005X04 | .R_0402_1k | 36 | Panasonic | ERJ-2GEJ102X | Mouser | 667-ERJ-2GEJ102X | 0.02
R_0402_2R | R2, R129 | RESC1005X04 | .R_0402_2R | 2 | Panasonic | ERJ-2GEJ2R0X | Mouser | 667-ERJ-2GEJ2R0X | 0.02
R_0402_10k | R4, R6, R7, R11, R13, R17, R23, R26, R28, R87, R88, R89, R90, R95, R96, R97, R102, R103 | RESC1005X04 | .R_0402_10k | 18 | Panasonic | ERJ-2GEJ103X | Mouser | 667-ERJ-2GEJ103X | 0.02
R_1206_2R_0.25% | R9, R21 | RESC3116X06 Shunt | .R_1206_2R_0.25% | 2 | Yageo | RT1206CRD072RL | Mouser | 603-RT1206CRD072RL | 0.35
R_0402_33R | R10, R16, R22, R69, R70, R71, R72, R73, R74, R75, R76, R77, R78, R81, R84, R85, R86 | RESC1005X04 | .R_0402_33R | 17 | Panasonic | ERJ-2GEJ330X | Mouser | 667-ERJ-2GEJ330X | 0.02
R_0402_210R_0.1% | R12, R29, R130 | RESC1005X04 | .R_0402_210R_0.1% | 3 | Yageo | RT0402BRD07210RL | Mouser | 603-RT0402BRD07210RL | 0.19
R_0402_10R | R19, R58 | RESC1005X04 | .R_0402_10R | 2 | Panasonic | ERJ-2GEJ100X | Mouser | 667-ERJ-2GEJ100X | 0.02
R_0402_100R | R20 | RESC1005X04 | .R_0402_100R | 1 | Panasonic | ERJ-2GEJ101X | Mouser | 667-ERJ-2GEJ101X | 0.02
R_0402_5k1_1% | R25, R107 | RESC1005X04 | .R_0402_5k1_1% | 2 | Panasonic | ERJ-2RKF5101X | Mouser | 667-ERJ-2RKF5101X | 0.02
R_0402_100k_1% | R30, R31, R32, R33, R34, R35, R36, R37, R38, R40, R42, R43, R44, R45, R46, R47, R48, R49, R50, R52, R54, R98, R101, R105, R111, R128 | RESC1005X04 | .R_0402_100k | 26 | Panasonic | ERJ-2RKF1003X | Mouser | 667-ERJ-2RKF1003X | 0.02
R_0402_470R | R39, R41, R51, R53, R100, R106, R109, R114, R115, R116, R117, R118, R119, R120, R121, R122, R123 | RESC1005X04 | .R_0402_470R_1% | 17 | Panasonic | ERJ-2RKF4700X | Mouser | 667-ERJ-2RKF4700X | 0.028
R_0402_24k | R99 | RESC1005X04 | .R_0402_24k | 1 | Panasonic | ERJ-2GEJ243X | Mouser | 667-ERJ-2GEJ243X | 0.02
R_0402_680k_1% | R104 | RESC1005X04 | .R_0402_680k_1% | 1 | Panasonic | ERJ-2RKF6803X | Mouser | 667-ERJ-2RKF6803X | 0.02
R_0402_240k_1% | R108, R110 | RESC1005X04 | .R_0402_240k_1% | 2 | Panasonic | ERJ-2RKF2403X | Mouser | 667-ERJ-2RKF2403X | 0.02
R_0402_0R_1% | R131, R132 | RESC1005X04-SEL | .R_0402_0R_1%_SEL | 2 | Panasonic | AC0402FR-070RL | Mouser | 603-AC0402FR-070RL | 0.02
T_BSH105 | T1, T2 | SOT95P230X110-3N | .T_BSH105 | 2 | Nexperia | BSH105,215 | Mouser | 771-BSH105215 | 0.21
OPA2388 | U1, U5 | TSOP65P490X110-8N | OPA2388 | 2 | TI | OPA2388IDGKR | Mouser | 595-OPA2388IDGKR | 2.63
UA_DAC8562-DSC | U2, U8 | PSON50P300X80_HS-11N | DAC8562-DSC | 2 | TI | DAC8562SDSCR | Mouser | 595-DAC8562SDSCR | 6.73
AD8421B | U3, U7 | TSOP65P490X110-8N | AD8421B | 2 | Analog | AD8421BRMZ | Mouser | 584-AD8421BRMZ | 8.10
ADS8691 | U4, U6, U9 | TSOP65P640X120-16N | ADS8691 | 3 | TI | ADS8691IPWR | Mouser | 595-ADS8691IPWR | 8.5
UA_OPA189-DBV | U10 | SOT95P280X145-5N | OPA189-DBV | 1 | TI | OPA189IDBVR | Mouser | 595-OPA189IDBVR | 2.02
UD_74LVC2T45-GT | U11, U12, U23, U24, U25, U26, U27, U28, U29 | SON50P100X50_HS-9N | 74LVC2T45GT | 9 | Nexperia | 74LVC2T45GT,115 | Mouser | 771-74LVC2T45GT115 | 0.37
UD_NLAS4684-FC | U13, U33, U35 | BGA12C50P4X3_196X146X65 | NLAS4684-FC | 3 | ON Semi | NLAS4684FCT1G | Mouser | 863-NLAS4684FCT1G | 0.80
TC7WH08FK | U14 | TSSOP50P310X80-8N | TC7WH08FK | 1 | Toshiba | TC7WH08FK,LJ(CT | Mouser | 757-TC7WH08FKLJCT | 0.24
HCT2G04 | U15 | SOT65P210X110-6N | HCT2G04 | 1 | Nexperia | 74HC2G04GW,125 | Mouser | 771-HC2G04GW125 | 0.21
UA_OPA388-DBV | U16, U32 | SOT95P280X145-5N | OPA388-DBV | 2 | TI | OPA388IDBVR | Mouser | 595-OPA388IDBVR | 1.80
UD_CAT24C256-HU | U17 | PSON50P300X55_HS-9N | CAT24C256-HU4 | 1 | ON Semi | CAT24C256HU4IGT3 | Mouser | 863-CAT24C256HU4IGT3 | 0.36
TPL5010 | U18 | SOT95P280X100-6N | TPL5010 | 1 | TI | TPL5010DDCR | Mouser | 595-TPL5010DDCR | 0.62
LP2989-5.0 | U19 | TSOP65P490X110-8N | LP2989-5.0 | 1 | TI | LP2989AIMM-5.0/NOPB | Mouser | 926-LP2989AIMM50NOPB | 2.05
MP3221 | U20 | SOT95P280X100-6N | MP3221 | 1 | MPS | MP3221GJ-Z | Mouser | 946-MP3221GJ-Z | 1.33
LP2989-3.3 | U21 | TSOP65P490X110-8N | LP2989-3.3 | 1 | TI | LP2989IMM-3.3/NOPB | Mouser | 926-LP2989IMM3.3NOPB | 2.27
LT3487 | U22 | PSON50P300X100_HS-11N | LT3487 | 1 | Analog | LT3487EDD#TRPBF | Mouser | 584-LT3487EDD#TRPBF | 2.72
UD_74HC4066-BQ | U30, U31 | PQFN50P250X300X100_HS-15N | 74HC4066BQ | 2 | Nexperia | 74HC4066BQ,115 | Mouser | 771-HC4066BQ115 | 0.27
UD_PI5A4158ZA | U34, U36, U37, U38, U39, U40, U41 | SON50P100X80_HS-13N | PI5A4158ZA | 7 | Diodes Inc | PI5A4158ZAEX | Mouser | 729-PI5A4158ZAEX | 0.36

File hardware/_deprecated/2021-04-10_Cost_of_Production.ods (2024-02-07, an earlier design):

Shop | Item | net price / € | Quantity | Result
Eurocircuits | PCB Shepherd Cape v2.0r0 with Stencil | 51,67 | 3 | 155,00
Eurocircuits | PCB Shepherd Cape v2.0r1 with Stencil | 14,06 | 32 | 450,00
Eurocircuits | PCB Shepherd Cape v2.1 with Stencil | 14,38 | 32 | 460,00
Eurocircuits | PCB nRF-Target v2.0 with Stencil | 4,84 | 32 | 155,00
Eurocircuits | PCB nRF-Target v2.1 with Stencil | 5,47 | 32 | 175,00
 |  |  |  | 0,00
Mouser | Parts for Shepherd-Cape without Recorder | 68,96 | 32 | 2206,72
Mouser | Parts for Shepherd-Cape ONLY Recorder | 42,11 | 3 | 126,33
Mouser | Parts for nRF-Target | 13,18 | 33 | 434,94
Digikey | Parts for Shepherd-Cape (Pinheaders) | 5,58 | 32 | 178,42
 |  |  |  | 0,00
Betalayout | Solder Paste | 23,00 | 1 | 23,00
 | SMD-Assembly (Estimate) | 46,88 | 30 | 1406,25
 |  |  |  | 0,00
Formulor | Casing (Estimate) | 15,00 | 30 | 450,00
 |  |  |  | 0,00
CSV | USB-Sticks 128 GB (div brands) for testing | 16,67 | 3 | 50,00
ComputerUniverse | USB-Stick 256 GB, Philips FM25FD75B/00 | 25,90 | 30 | 777,00
CSV | POE-Adapter Kit for testing (TP-Link) | 21,00 | 1 | 21,00
alternate | POE-Splitter (TP-POE10R) | 11,00 | 30 | 330,00
rs-online | Bbone Green | 47,00 | 30 | 1410,00
ComputerUniverse | SD-Cards for flashing (PNY Pro Elite 32 GB) | 10,74 | 5 | 53,70
alternate | LAN-Cables 10-20cm (BB to POE) | 2,40 | 30 | 72,00
rs-online | LAN-Cables 50 - 300cm (POE to Wall) | 3,35 | 30 | 100,50
?kai? | Bbone AI for evaluation | 110,00 | 2 | 220,00
 |  |  |  | 0,00
 | Cisco Switch | 5907,00 | 0 | 0,00
 |  |  | SUM: | 9.254,86 €
ColorCoding
Blue Items | needed during dev
Orange Items | Estimate - not ordered yet

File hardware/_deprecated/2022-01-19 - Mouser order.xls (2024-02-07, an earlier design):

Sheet: Sheet1
Comment | Manufacturer | Manufacturer PN | Distributer PN | Price [€] | Quantity
74LVC2T45GM | Nexperia | 74LVC2T45GM,125 | 771-74LVC2T45GM125 | 0.406 | 100
100 R | Panasonic | ERJ-2GEJ101X (https://www.mouser.de/ProductDetail/Panasonic/ERJ-2GEJ101X?qs=Cz%252B5TvT4ylzvFLU04D2DFQ%3D%3D) | 667-ERJ-2GEJ101X | 0.02 | 50
430 R | Panasonic | ERJ-2GEJ431X (https://www.mouser.de/ProductDetail/Panasonic/ERJ-2GEJ431X?qs=YMBIwoNQYdWkvumG%2FWRq4g%3D%3D) | 667-ERJ-2GEJ431X | 0.02 | 50
1 k | Panasonic | ERJ-2GEJ102X | 667-ERJ-2GEJ102X | 0.02 | 50
2 k | Yageo | AC0402JR-072KL (https://www.mouser.de/ProductDetail/YAGEO/AC0402JR-072KL?qs=ygRr%2Ftkhtet40d8iOckJVQ%3D%3D) | 603-AC0402JR-072KL | 0.02 | 50
2.7 k | Yageo | AC0402FR-072K7L (https://www.mouser.de/ProductDetail/YAGEO/AC0402FR-072K7L?qs=yhV1fb9g%2FKY0mUoSgfHwLw%3D%3D) | 603-AC0402FR-072K7L | 0.02 | 50
100 k | Yageo | AF0402FR-07100KL (https://www.mouser.de/ProductDetail/YAGEO/AF0402FR-07100KL?qs=HEu%2FF%2FCqxzIuS6oTgJlL0A%3D%3D) | 603-AF0402FR-07100KL | 0.03 | 50
1 M | Panasonic | ERJ-2GEJ105X (https://www.mouser.de/ProductDetail/Panasonic/ERJ-2GEJ105X?qs=H7k1u0Mp9JQDA6YNNR2WyQ%3D%3D) | 667-ERJ-2GEJ105X | 0.02 | 50
3.3 M | Panasonic | ERJ-2GEJ335X (https://www.mouser.de/ProductDetail/Panasonic/ERJ-2GEJ335X?qs=MVjVSMjNRMqJ%2FrpuVtP9Pg%3D%3D) | 667-ERJ-2GEJ335X | 0.02 | 50
10 M | Panasonic | ERJ-2GEJ106X (https://www.mouser.de/ProductDetail/Panasonic/ERJ-2GEJ106X?qs=6%252BUraArZVSBCZmk3hNWmDQ%3D%3D) | 667-ERJ-2GEJ106X | 0.02 | 50
1 nF | Murata | GRM1555C1H102JA01D | 81-GRM1555C1H102JA1D | 0.02 | 50
10 nF | Murata | GCM155R71E103KA37D | 81-GCM155R71E103KA7D | 0.02 | 50
100 nF | Taiyo Yuden | EMF105B7104MVHF | 963-EMF105B7104MVHF | 0.03 | 100
1 uF 25V | Murata | GRM155R61E105KA12J | 81-GRM155R61E105KA2J | 0.06 | 100
4.7 uF 6V3 | Murata | GRM155R60J475ME87D (https://www.mouser.de/ProductDetail/Murata-Electronics/GRM155R60J475ME87D?qs=pTGEtN%252BMLlBnU9jM8bPB0Q%3D%3D) | 81-GRM155R60J475ME8D | 0.05 | 50
10 uF 4V0 | Murata | GRM155R60G106ME01D (https://www.mouser.de/ProductDetail/Murata-Electronics/GRM155R60G106ME01D?qs=d0WKAl%252BL4KYRfB4EgQksjw%3D%3D) | 81-GRM155R60G106ME1D | 0.09 | 50
alternative | TI | OPA2388IDGKT | 595-OPA2388IDGKT | 3.43 | 40
alternative | Nexperia | 74HC2G04GW-Q100H | 771-74HC2G04GW-Q100H | 0.37 | 40
alternative | TI | OPA388IDBVT | 595-OPA388IDBVT | 2.52 | 40
alternative | TI | TPL5010DDCR | 595-TPL5010DDCT | 0.98 | 40
alternative | TI | OPA189IDBVT | 595-OPA189IDBVT | 2.47 | 40

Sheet: Sheet2
Distributer PN | Quantity
771-74LVC2T45GM125 | 100
667-ERJ-2GEJ101X | 50
667-ERJ-2GEJ431X | 50
667-ERJ-2GEJ102X | 50
603-AC0402JR-072KL | 50
603-AC0402FR-072K7L | 50
603-AF0402FR-07100KL | 50
667-ERJ-2GEJ105X | 50
667-ERJ-2GEJ335X | 50
667-ERJ-2GEJ106X | 50
81-GRM1555C1H102JA1D | 50
81-GCM155R71E103KA7D | 50
963-EMF105B7104MVHF | 100
81-GRM155R61E105KA2J | 100
81-GRM155R60J475ME8D | 50
81-GRM155R60G106ME1D | 50
595-OPA2388IDGKT | 40
771-74HC2G04GW-Q100H | 40
595-OPA388IDBVT | 40
595-TPL5010DDCT | 40
595-OPA189IDBVT | 40

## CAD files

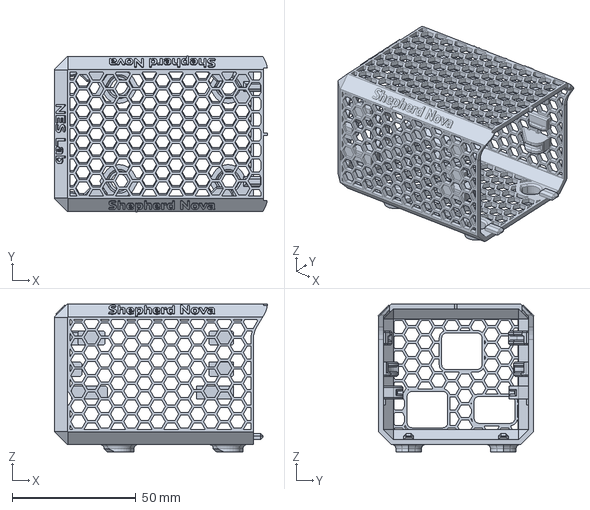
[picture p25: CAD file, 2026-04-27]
hardware/observer_case_3DPrinted/Part Studio 1 - CaseMain.step
86.1 x 62.9 x 59.8 mm

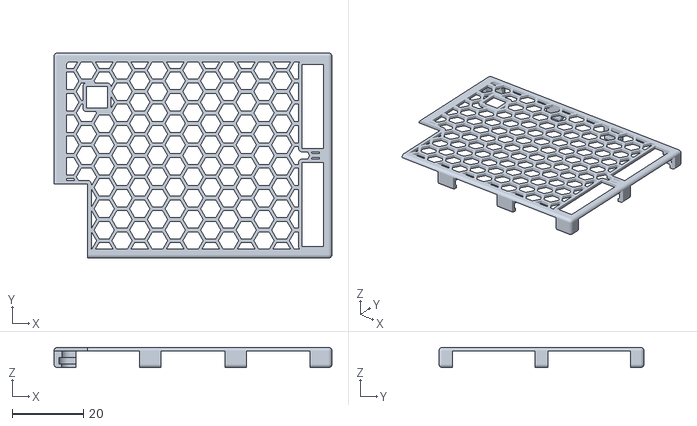
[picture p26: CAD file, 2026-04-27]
hardware/cape_v2.5_cage/cape_v25_cage.stl
78.3 x 57.8 x 5.70

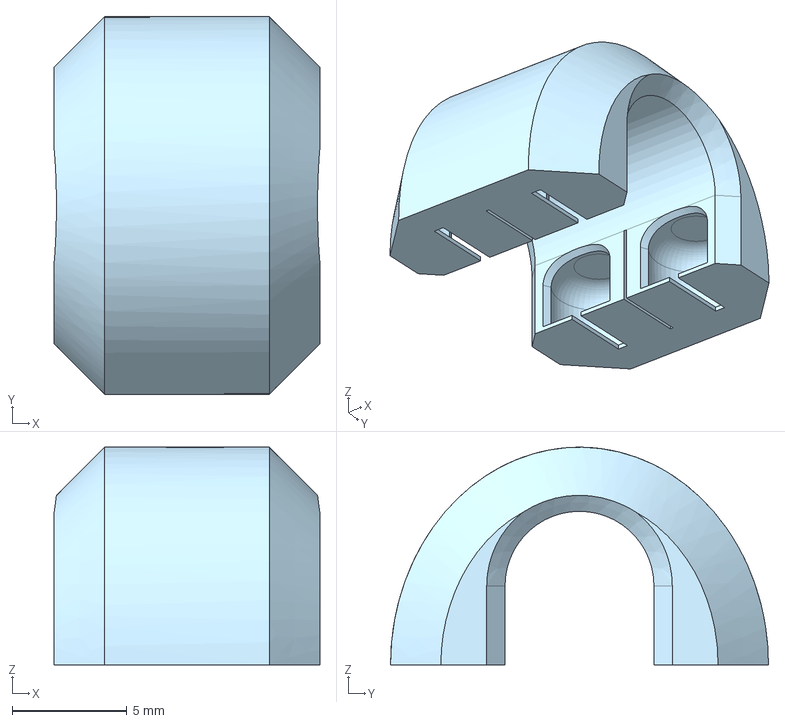
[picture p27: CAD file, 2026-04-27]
hardware/network_cable_clip/NW CableClip.step
11.6 x 16.5 x 9.50 mm

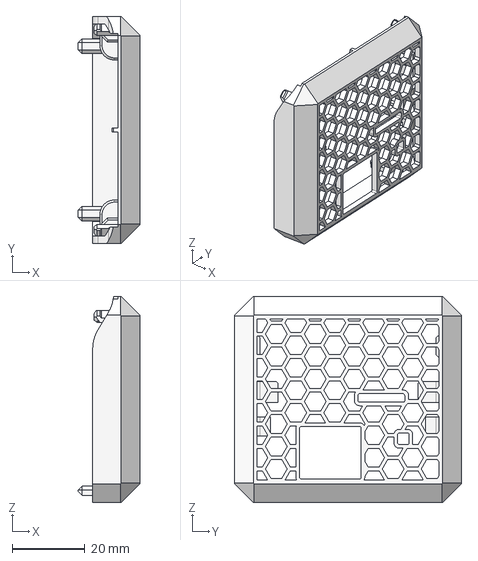
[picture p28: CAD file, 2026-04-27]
hardware/observer_case_3DPrinted/Part Studio 1 - CaseBack.step
17.0 x 62.6 x 56.8 mm

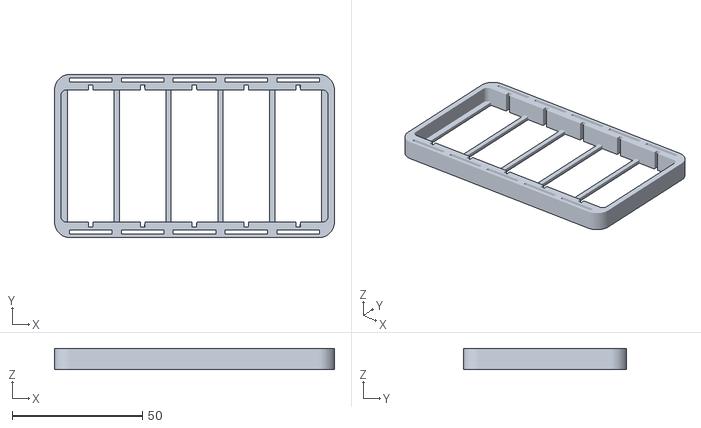
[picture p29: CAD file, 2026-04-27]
hardware/pcb_bulk_holder/shepherd-cape-bulk-holder.stl
107.5 x 62.7 x 8.10

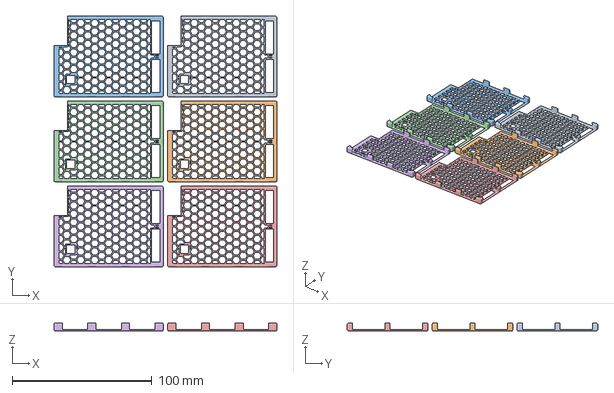
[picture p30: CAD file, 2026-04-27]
hardware/cape_v2.5_cage/cape_cage_PLA_x6.3mf
159.6 x 179.4 x 5.70 mm
cape_v25_cage_.stl x 6

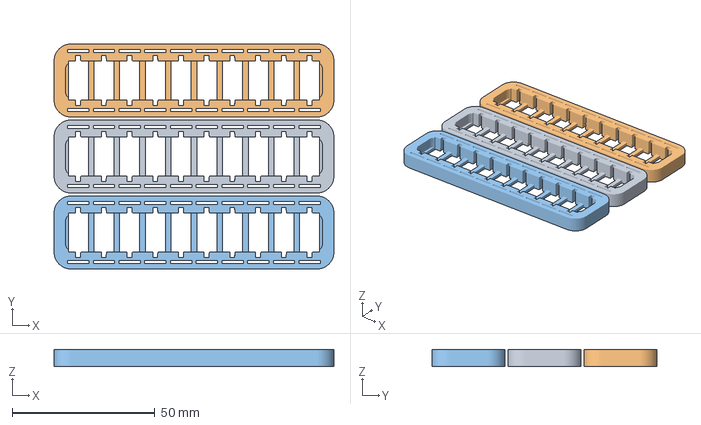
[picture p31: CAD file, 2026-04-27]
hardware/pcb_bulk_holder/shepherd-target-bulk-holder.3mf
98.0 x 78.8 x 6.10 mm
shepherd-target-holder.stl x 3

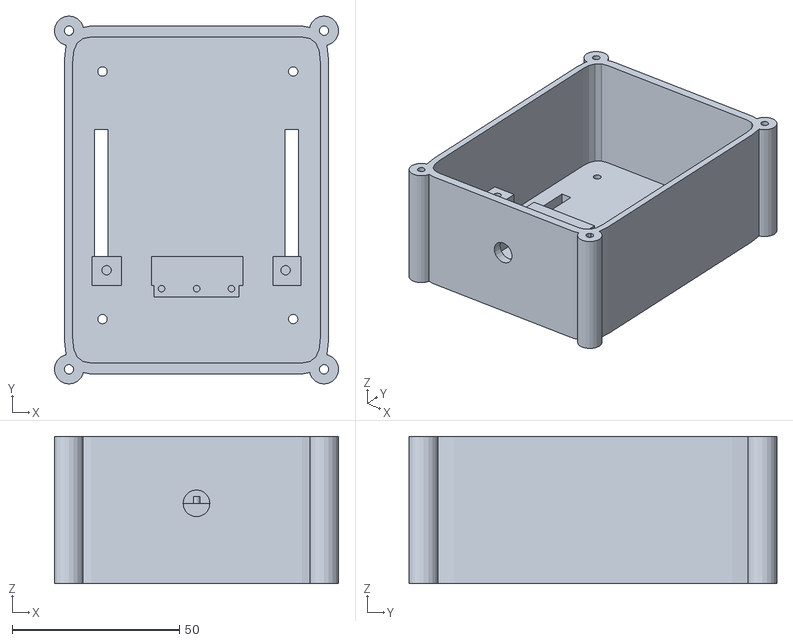
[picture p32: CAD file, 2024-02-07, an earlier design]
hardware/_deprecated/housing_v1/harvester/piezo_harvester_case.stl
85.0 x 110.0 x 44.0

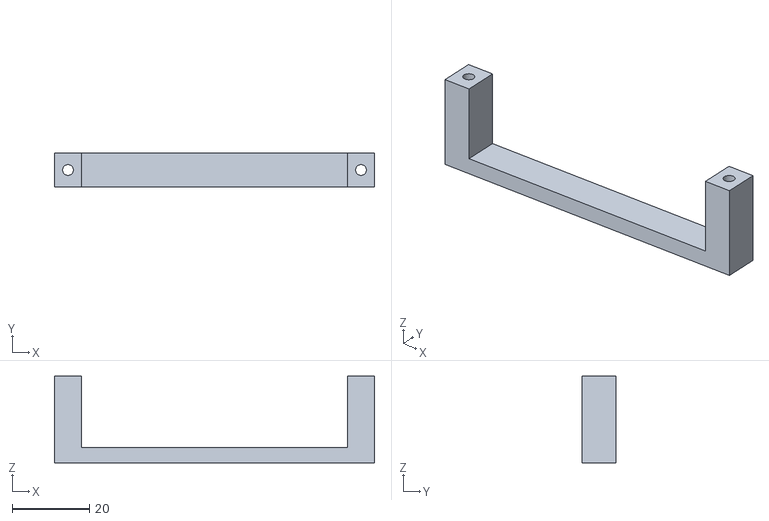
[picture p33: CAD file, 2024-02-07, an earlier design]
hardware/_deprecated/housing_v1/shepherd/clamp_powerbank_belt.stl
83.0 x 8.80 x 22.5

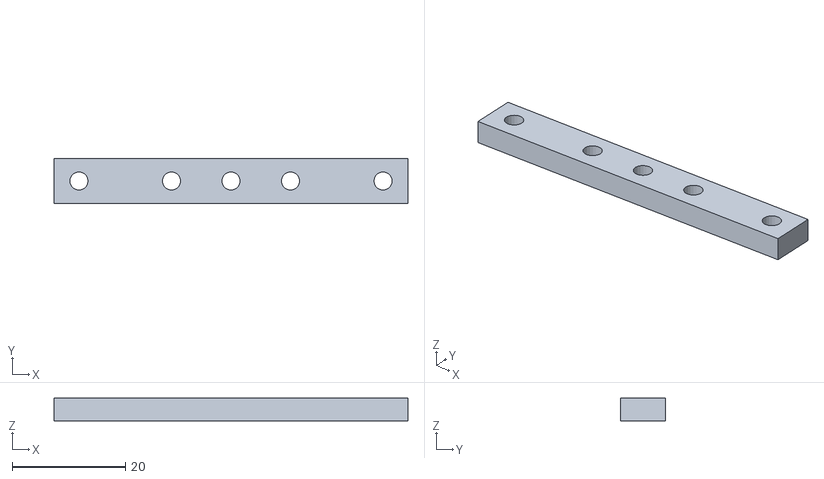
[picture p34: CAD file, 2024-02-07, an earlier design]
hardware/_deprecated/housing_v1/harvester/piezo_harvester_clamp.stl
62.5 x 8.00 x 4.00

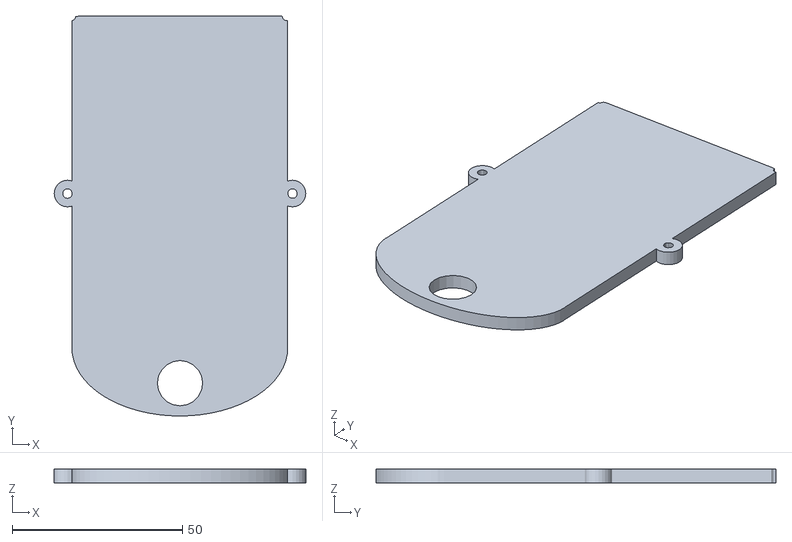
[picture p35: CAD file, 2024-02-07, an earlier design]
hardware/_deprecated/housing_v1/shepherd/shepherd_cover.stl
74.0 x 117.6 x 4.00

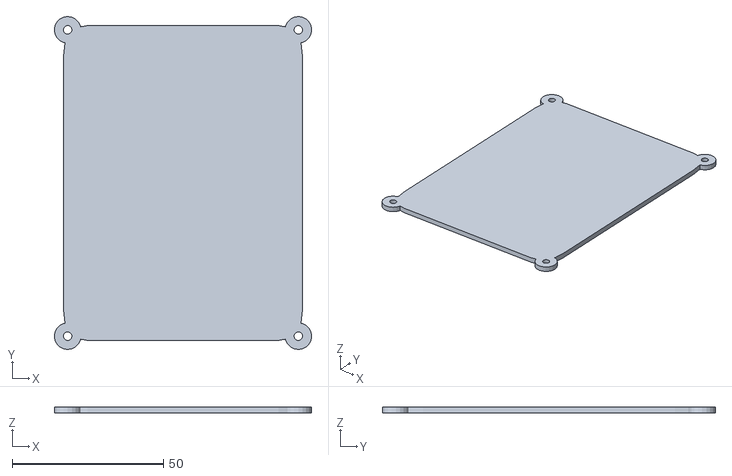
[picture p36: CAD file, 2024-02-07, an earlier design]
hardware/_deprecated/housing_v1/harvester/piezo_harvester_cover.stl
85.0 x 110.0 x 2.00

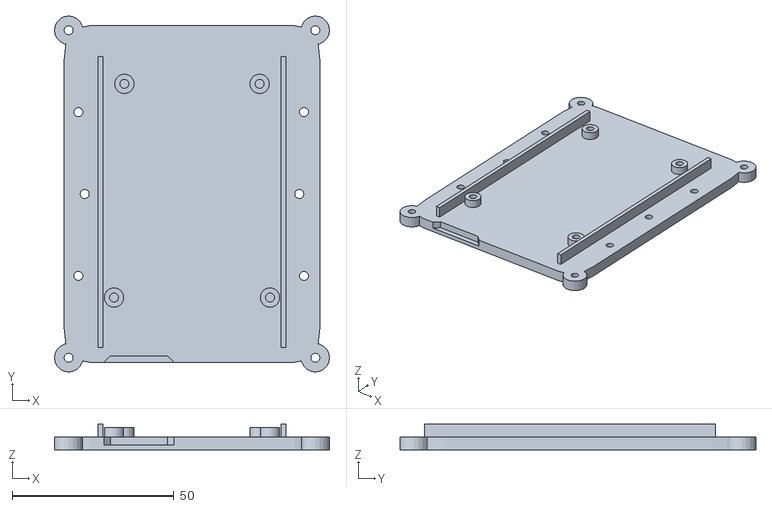
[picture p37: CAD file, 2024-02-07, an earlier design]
hardware/_deprecated/housing_v1/shepherd/shepherd_plate.stl
85.0 x 110.0 x 8.00

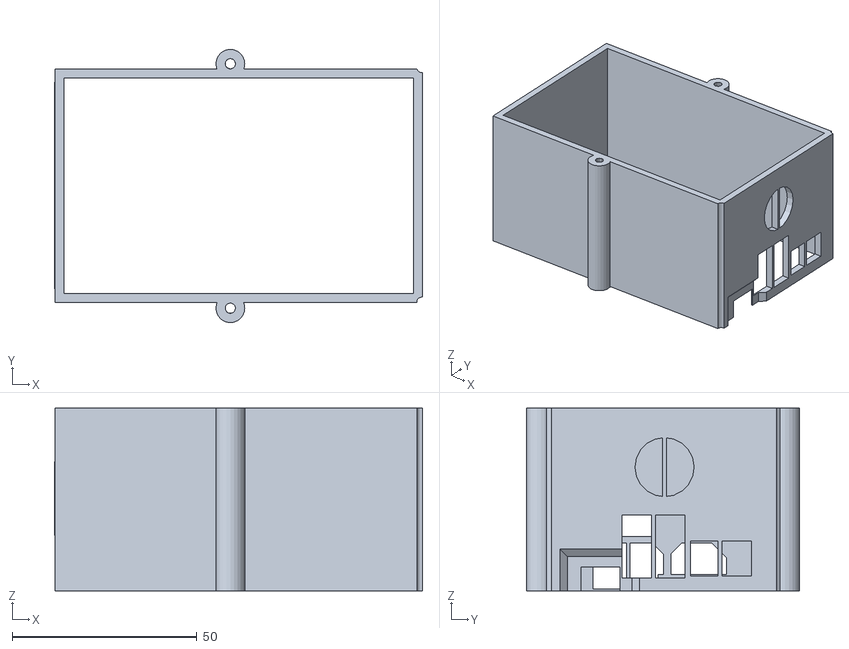
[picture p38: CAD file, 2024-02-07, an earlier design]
hardware/_deprecated/housing_v1/shepherd/shpherd_wall.stl
99.6 x 74.0 x 49.5

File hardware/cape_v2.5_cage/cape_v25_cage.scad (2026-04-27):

pcb_x = 75.3;
pcb_y = 54.8;
pcb_z1 = 1.8;
pcb_z2 = 3.7;

hdr_x = 82.6 - pcb_x/2 - 11.2;
hdr_y = 41.2 - pcb_y/2;

hrv_x = 21.8 - pcb_x/2 - 11.2;
hrv_y = 43.8 - pcb_y/2;

include <misc_parts.scad>


module cape25()
{
    // cutouts
    union() {
        //import("shepherd_pcb_v25a.stl", convexity=100)
        // PCB + Parts (large cutout)
        translate([0,0,pcb_z1/2]) round_cuboid(x=pcb_x+0.1, y=pcb_y+0.1, z=pcb_z1+0.1,r=2.54, $fn=100);
        translate([0,0,pcb_z2/2]) round_cuboid(x=pcb_x-2*0.6, y=pcb_y-2*0.6, z=pcb_z2,r=2.54, $fn=100);
        // cutout below
        translate([0,0,-pcb_z2/2]) round_cuboid(x=pcb_x-2*0.5, y=pcb_y-2*0.5, z=pcb_z2,r=2.54, $fn=100);

        // TargetHeaders
        translate([hdr_x,+hdr_y,pcb_z1+10/2]) cube([6,23.6,10], center=true);
        translate([hdr_x,-hdr_y,pcb_z1+10/2]) cube([6,23.6,10], center=true);
        // PWR & USB
        translate([-(pcb_x-8)/2,-17,pcb_z1+10/2]) cube([8,18,10], center=true);
        translate([-pcb_x/2,-20,pcb_z2]) cube([2*8,24,15], center=true);
        // harvester
        translate([hrv_x,hrv_y,pcb_z1+10/2]) cube([6,6,10], center=true);
        // NW
        translate([-pcb_x/2 - 1.5,0,0]) cube([22,16,2*pcb_z2], center=true);

        // cutouts horizontal
        translate([0,+(4+23)/2,0]) cube([pcb_x + 10,23.2,2*pcb_z2], center=true);
        translate([0,-(4+23)/2,0]) cube([pcb_x + 10,23.2,2*pcb_z2], center=true);

        // cutouts vertical
        translate([+24.0,0,0]) cube([18,pcb_y+10,2*pcb_z2], center=true);
        translate([0.0,0,0]) cube([18,pcb_y+10,2*pcb_z2], center=true);
        translate([-24.0,0,0]) cube([18,pcb_y+10,2*pcb_z2], center=true);
    }
}

module window_honey_neg()
{
    // honey comb top
    // easy way to tune line-thickness -> d_cylinder
    intersection () {
        difference () {
            translate([0,0,pcb_z2]) round_cuboid(x=pcb_x-4.0, y=pcb_y-2.0, z=pcb_z2,r=1, $fn=100);
            // border for connectors (+2mm)
            // TargetHeaders
            translate([hdr_x,+hdr_y,pcb_z1+10/2]) round_cuboid(x=6+2,y=23.6+2,z=10,r=1);
            translate([hdr_x,-hdr_y,pcb_z1+10/2]) round_cuboid(x=6+2,y=23.6+2,z=10,r=1);
            // PWR & USB
            translate([-(pcb_x-8)/2,-17,pcb_z1+10/2]) round_cuboid(x=8+2,y=18+2,z=10,r=1);
            // harvester
            translate([hrv_x,hrv_y,pcb_z1+10/2]) round_cuboid(x=6+2,y=6+2,z=10, r=1);
            }

        for (i = [-10:1:10], j=[-10:1:10]) {
            translate([i*5.0,i*3.0 + j*6,0]) cylinder(h=25, d=5.7, $fn=6);
        }
    }
}

module cage()
{
    difference () {
        translate([0,0,pcb_z2/2]) round_cuboid3(x=pcb_x+2*1.5, y=pcb_y+2*1.5, z=pcb_z2+2*1,r=1, $fn=100);
        window_honey_neg();
        cape25();
    }
}


//cape25();
//window_honey_neg();
cage();

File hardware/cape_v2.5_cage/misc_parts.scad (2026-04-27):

/*
Info:
This lib contains things like screws, nuts and bearings.

Improvement:
- wasn't there before

TODO:
- differentiate between parts that get subtracted and normal parts (different diameters)

*/

M3_screw_hole_dia = 3.4;
M3_nut_hole_dia   = 6.2+0.2;

M4_screw_hole_dia = 4.4;
M4_nut_hole_dia   = 7.7+0.2;

module screw_M3(length)
{
    cylinder(d=M3_screw_hole_dia, h=length);
	cylinder(d=M3_nut_hole_dia, h=2.3, center=true, $fn=6);
}

module screw_M4(length)
{
    cylinder(d=M4_screw_hole_dia, h=length);
	cylinder(d=M4_nut_hole_dia, h=3.3, center=true, $fn=6);
}


// Bearing - inner Diameter, outer diameter, width
module bearing(ID,OD,W)
{
    translate([0,0,W/2]) difference()
    {
        cylinder(d=OD, h=W, center=true);
        cylinder(d=ID, h=W+1, center=true);
    }
}

// unregular cube
// 4 of the 12 edges are rounded
module round_cuboid(x,y,z,r,$fn=48)
{
    cube([x,y-2*r,z],center=true);
    cube([x-2*r,y,z],center=true);
    cube([x-2*r,y-2*r,z],center=true);

    translate([+x/2-r,+y/2-r,0]) cylinder(r=r,h=z,center=true);
    translate([+x/2-r,-y/2+r,0]) cylinder(r=r,h=z,center=true);
    translate([-x/2+r,+y/2-r,0]) cylinder(r=r,h=z,center=true);
    translate([-x/2+r,-y/2+r,0]) cylinder(r=r,h=z,center=true);
}

// unregular cube
// all 12 edges are rounded
module round_cuboid3(x,y,z,r,$fn=48)
{
    cube([x,y-2*r,z-2*r],center=true);
    cube([x-2*r,y,z-2*r],center=true);
    cube([x-2*r,y-2*r,z],center=true);

    translate([+x/2-r,+y/2-r,0]) cylinder(r=r,h=z-2*r,center=true);
    translate([+x/2-r,-y/2+r,0]) cylinder(r=r,h=z-2*r,center=true);
    translate([-x/2+r,+y/2-r,0]) cylinder(r=r,h=z-2*r,center=true);
    translate([-x/2+r,-y/2+r,0]) cylinder(r=r,h=z-2*r,center=true);

    translate([+x/2-r,0,+z/2-r]) rotate([90,0,0]) cylinder(r=r,h=y-2*r,center=true);
    translate([+x/2-r,0,-z/2+r]) rotate([90,0,0]) cylinder(r=r,h=y-2*r,center=true);
    translate([-x/2+r,0,+z/2-r]) rotate([90,0,0]) cylinder(r=r,h=y-2*r,center=true);
    translate([-x/2+r,0,-z/2+r]) rotate([90,0,0]) cylinder(r=r,h=y-2*r,center=true);

    translate([0,+y/2-r,+z/2-r]) rotate([0,90,0]) cylinder(r=r,h=x-2*r,center=true);
    translate([0,+y/2-r,-z/2+r]) rotate([0,90,0]) cylinder(r=r,h=x-2*r,center=true);
    translate([0,-y/2+r,+z/2-r]) rotate([0,90,0]) cylinder(r=r,h=x-2*r,center=true);
    translate([0,-y/2+r,-z/2+r]) rotate([0,90,0]) cylinder(r=r,h=x-2*r,center=true);

    translate([+(x/2-r),+(y/2-r),+(z/2-r)]) sphere(r=r);
    translate([+(x/2-r),+(y/2-r),-(z/2-r)]) sphere(r=r);
    translate([+(x/2-r),-(y/2-r),+(z/2-r)]) sphere(r=r);
    translate([+(x/2-r),-(y/2-r),-(z/2-r)]) sphere(r=r);
    translate([-(x/2-r),+(y/2-r),+(z/2-r)]) sphere(r=r);
    translate([-(x/2-r),+(y/2-r),-(z/2-r)]) sphere(r=r);
    translate([-(x/2-r),-(y/2-r),+(z/2-r)]) sphere(r=r);
    translate([-(x/2-r),-(y/2-r),-(z/2-r)]) sphere(r=r);
}

//round_cuboid3(20,10,15,2);

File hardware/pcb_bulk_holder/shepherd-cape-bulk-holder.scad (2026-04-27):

// Classic Wall Generator needs +0.15, Arachne more like +0.30
plug_dim = [1.6 + 0.25, 54.4 + 0.30, 8 + 0.2];
plug_distance = 19.9;
plug_count = 5;
d_clamp = 20;
s_clamp = 0.20; // narrowing on both sides

$fn=48;

module round_cuboid(x,y,z,r)
{
    cube([x,y-2*r,z],center=true);
    cube([x-2*r,y,z],center=true);
    cube([x-2*r,y-2*r,z],center=true);

    translate([+x/2-r,+y/2-r,0]) cylinder(r=r,h=z,center=true);
    translate([+x/2-r,-y/2+r,0]) cylinder(r=r,h=z,center=true);
    translate([-x/2+r,+y/2-r,0]) cylinder(r=r,h=z,center=true);
    translate([-x/2+r,-y/2+r,0]) cylinder(r=r,h=z,center=true);
}


difference () {
    case_x = 8 + plug_count * plug_distance;
    case_y = 8 + plug_dim[1];
    case_z = plug_dim[2] - 0.1;
    round_cuboid(case_x, case_y, case_z, 6);

    translate([0,0,0.99]) round_cuboid(case_x-5, case_y-12, case_z-1, 2);

    plug_range = (plug_count - 1) / 2;
    narrowing_x = (d_clamp/2 + plug_dim[0]/2 - s_clamp);
    narrowing_y = (plug_dim[1] - .1) / 2;
    clamp_xyz = [plug_distance-3.5,1.5,plug_dim[2]];
    slot_xyz = [plug_distance-2.0, case_y-8-4.0, case_z+1];
    for (i = [-plug_range:1:plug_range]) {
        translate([i*plug_distance,0,0])     difference() {
            // usb-plug
            cube(plug_dim, center=true);
            // a narrow clamping piece on both sides
            translate([+narrowing_x,+narrowing_y,0]) sphere(d=d_clamp,$fn=120);
            translate([+narrowing_x,-narrowing_y,0]) sphere(d=d_clamp,$fn=120);
            //translate([-narrowing_x,+narrowing_y,0]) sphere(d=d_clamp,$fn=120);
            //translate([-narrowing_x,-narrowing_y,0]) sphere(d=d_clamp,$fn=120);

        }
        // a slot for some spring clamping
        translate([i*plug_distance,+plug_dim[1]/2 + 1.8,0]) cube(clamp_xyz, center=true);
        translate([i*plug_distance,-plug_dim[1]/2 - 1.8,0]) cube(clamp_xyz, center=true);
        translate([i*plug_distance,0,0]) cube(slot_xyz, center=true);
        }
    }

/*
difference () {
    round_cuboid(12, 22, 5.5, 3);
    difference() {
        // usb-plug and a narrow clamping piece on both sides
        cube(plug_dim, center=true);
        translate([+(d_clamp/2 + plug_dim[0]/2 - s_clamp),0,0]) sphere(d=d_clamp,$fn=160);
        translate([-(d_clamp/2 + plug_dim[0]/2 - s_clamp),0,0]) sphere(d=d_clamp,$fn=160);
    }
}
*/

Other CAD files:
hardware/pcb_bulk_holder/shepherd-target-bulk-holder.scad
hardware/pcb_bulk_holder/shepherd-target-bulk-holder.stl

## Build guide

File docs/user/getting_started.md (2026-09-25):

# Getting started

This section describes how to set up a shepherd-instance in a tethered setup.

## Prerequisites

To set up an instance of shepherd, you'll need to assemble a number of shepherd observers.

For each node, you'll need:

* BeagleBone (Green/Black)
* shepherd cape

  * for recording: harvesting transducer, e.g. solar cell
  * for emulation: target board

In addition, you'll need at least one SD-card with at least 4GB capacity. To setup linux and control the nodes a linux host-machine is recommended, but the terminal in macOS or WSL on Windows should work as well.

For details to the cape and additional hardware take a look at the [hardware section](./hardware.md).

The shepherd cape has a large number of small components. We suggest to send it to a PCB fab for assembly.

If you don't have the necessary resource or need assistance with getting the hardware manufactured, get in touch with the developers.

To connect the shepherd observers to each other for control, data collection and time-synchronization, you need to set up an Ethernet network.
The network should be as flat as possible, i.e. have a minimum number of switches. This prevents possible trouble and also improves time synchronization with ptp. For sub 1 us offsets a hardware accelerated switch (like the Cisco Catalyst Series) is beneficial.
By default, the BeagleBone Ubuntu image is configured to request an IP address by DHCP.
Therefore, your network should have a DHCP server.

## Hardware setup

Stack the cape on top of the BeagleBone. The two 23×2 headers of the cape plug into the BeagleBone (P8 and P9). Additionally, connect a harvesting source or target board to the cape.
Pay attention to the 2×2 harvesting header P6 on the cape. The corresponding signal labels are printed on the backside.
Stack the target PCB on top of the shepherd cape. The cape offers two ports P10 and P11 on the right side, additionally labeled A & B.

Provide all BeagleBones with power through either the USB type C port on the cape or the screw in connector right below it. Also connect the Ethernet ports to an Ethernet switch.
Using a PoE switch and corresponding power splitters can greatly reduce the cabling requirements. These can introduce noise into the system though. We designed an additional filtering regulator to allow input voltages up to 17 V that can be put in between.

The DHCP server and your machine (for installation/control) must be connected to the same network.

## Installation - Images

Shepherd is been tested and used on Debian based distributions. Fresh images can be sourced from the [rcn-ee](https://rcn-ee.com/rootfs/)-repo. Be sure to select the ones that `armhf`, `base` or `minimal`, `-ti` and `am335x` in the name / path. The following overview gives some recommendations. Be aware that this repo is updated constantly and links may break. Time of writing is 2024-07-08.

- [Debian 12 Bookwork](https://rcn-ee.com/rootfs/debian-armhf-12-bookworm-minimal-v6.1-ti/) is tested, fully working and recommended. It comes with python 3.11
- Debian 13 Trixie does NOT work due to issues downgrading the kernel to 4.19 (irrelevant due to switch to kernel 6.1)
- ~[Ubuntu 20.04](https://rcn-ee.com/rootfs/ubuntu-armhf-20.04-console-v5.10-ti/)~ is not supported anymore, due to the outdated bundled python 3.8
- [Ubuntu 22.04](https://rcn-ee.com/rootfs/ubuntu-armhf-22.04-console-v5.10-ti/) is tested and working, but not recommended anymore, due to the outdated bundled python 3.10
- ~[Ubuntu 24.04](https://rcn-ee.com/rootfs/ubuntu-armhf-24.04-console-v5.10-ti/)~ is not supported yet. It comes with the newest python 3.12, but does not properly boot with `linux-image-4.19.x`

NOTE: you can also choose to download pre-configured shepherd-images. See the more entry-friendly guide below.

## Installation - Full Guide

Prepare the SD-cards with the selected image.
If you plan to install the OS and shepherd software on the onboard EMMC flash, you can prepare one SD card and sequentially flash the nodes.
If you plan to install the OS and shepherd software on SD card, you have to prepare one SD card for every observer.
Depending on your choice, follow [the official instructions](https://elinux.org/BeagleBoardUbuntu#eMMC:_All_BeagleBone_Variants_with_eMMC) for **BeagleBone**. There is also a simplified and more detailed install-instruction in the following section.

After installing the OS on the BeagleBones and booting them, determine their IP addresses.
If you know the subnet, you can use nmap from your machine, for example:

```Shell
nmap 192.168.178.0/24
```

Clone the shepherd repository to your machine:

```Shell
git clone https://github.com/nes-lab/shepherd.git
```

Add an inventory file in the `inventory` folder in the repository, assigning hostnames to the IP addresses of the shepherd observers.
Just start by editing the provided `inventory/herd.yaml` example.
Pick a username that you want to use to log in to the system and assign as `ansible_user` variable.

```yaml
sheep:
  hosts:
    sheep0:
      ansible_host: 192.168.1.100
    sheep1:
      ansible_host: 192.168.1.101
    sheep2:
      ansible_host: 192.168.1.102
  vars:
    ansible_user: jane
  ptp_servers:
    hosts:
      sheep0:
  ptp_clients:
    hosts:
      sheep[1:30]:
```

:::{note}
Deployment supports roles that can be assigned directly in `herd.yaml`.
The example above shows how to use them exemplary by setting up `sheep0` as a PTP-Server (`ptp_servers`) and the remaining nodes as Clients (`ptp_clients`).
Additional roles are called `ntp_clients`, `gps_clients` and `secured`. The last one is used to reduce the attack surface when used in a testbed by removing default accounts, open ports and other listeners.
:::

We'll use [Ansible](https://www.ansible.com/) to roll out a basic configuration to the nodes.
This includes setting the hostname, adding the user, allowing password-less ssh access and sudo without password.
Make sure that you have `Python >=3.6`, `pip` and `sshpass` installed on your machine.
Install `Ansible` with:

```Shell
pip3 install ansible
```

Navigate to the root-directory of the cloned shepherd-project.
Now run the *bootstrap* [Ansible playbook](https://docs.ansible.com/ansible/latest/user_guide/playbooks_intro.html) using the previously prepared inventory file:

```Shell
ansible-playbook deploy/bootstrap.yml
```

To streamline the installation process, the shepherd software is installed via ansible as well. The **deployment** playbook allows to easily automate this process on a group of nodes.

```Shell
ansible-playbook deploy/deploy.yml
```

On success, the nodes will reboot and should be ready for use, for example, using the *shepherd-herd* command line utility.

Further playbooks:

- `maintenance.yml` will handle updates, some configuration, remove clutter, improve ram-usage and boot-duration
- `fetch-hostkeys.yml` will copy keys from nodes, handy firmware resets, while keeping keys
- `setup_pwdless_ssh_for_host.yml` will deposit your machines' certificates on the nodes for future passwordless login
- `setup-dev-nfs.yml` establish a local network file system `/opt/shepherd-dev` for the nodes to access
- `setup-ext-storage.yml` will format and automount sd-card to `/var/shepherd/recordings`
- `dev_rebuild_sw.yml` hot-swaps pru-firmware (& kernel-module & py-package) by compiling and flashing without restart

## Installation - ready-to-use image

The following guide sets up a single observer by deploying a ready-to-use shepherd-image. The steps are more detailed and try to simplify the process for new users by cutting away the first instructions from the installation-guide in the previous section (up to shepherd-deploy with ansible). The guide is written for **Windows 10 (or newer)** as host. Linux users can easily adapt.

As new hardware and unknown software can be intimidating the steps were also [filmed and put on YouTube](https://youtu.be/UPEH7QODm8A) for comparing the progress.

First step is downloading the [current shepherd-image](https://drive.google.com/drive/folders/1HBD8D8gC8Zx3IYpiVImVOglhO_RTwGYx) and flashing it to a micro-sd-card with [balenaEtcher](https://etcher.balena.io/) in admin mode. Note that other tools like rufus probably don't work. Select the (still compressed `.img.xz`) image and choose the appropriate drive to begin flashing.

Insert the prepared sd-card into the Beaglebone, connect the device via ethernet-cable to your local network and finally power the Beaglebone with a USB-Wall-Charger or any other power source with 5V and at least 500 mA.

After power-up all **LEDs** should light up immediately for ~1s. From then on the outermost LED acts as a permanent heartbeat and the other 3 LEDs show different IO usage. Boot is finished when the LEDs stop being busy (~30s). After that you can log in.

How to connect? There are at least three options. In most cases you can access the system by using the hostname `sheep0`. If that does not work you can check the list of network-devices compiled by your routers webinterface. Alternatively you can scan your local IP-space with an ip scanner, in our example the `Angry IP Scanner` was used. Look for the hostname `sheep0` or the MAC-Vendor `Texas Instruments` in the list. **Be sure to use the IP-space of the correct network device of your host device - there might be more than one**.

Configure WSL on Windows with a Linux of your choice (we recommend a generic Ubuntu) or you can use the PowerShell if OpenSSH is installed as an optional feature (`windows > settings > apps > optional features`).

The commands below open a secure shell (ssh) to the Beaglebone. As it's an unknown device you have to accept a new fingerprint (or host key) **once** before entering the password `temppwd` of the Beaglebone. The console will also tell you the password while trying to log in. Notice how the current console-line now begins with `ubuntu@sheep0`. It means you are logged in and every issued command will be executed on the Beaglebone. To **quit the shell** type `exit` (remember for later).

```Shell
# login via host-name (requires local DNS)
ssh ubuntu@sheep0
# or IP-based (replace IP from your setup)
ssh ubuntu@10.0.0.10
```

Now it is recommended to check if ubuntu was indeed started from the sd-card as the Beaglebones own flash-storage could contain & boot an old OS.

```Shell
uname -a
# ⤷ the string should contain "6.18." & "focal"
ll /dev/mmc*
# ⤷ should show mmcblk0* (SD-Card) and mmcblk1* (internal eMMC)
mount
# ⤷ should show that /dev/mmcblk0p1 (SD-Card) is "/" (root-directory) usually on line 1
```

If the tests are positive it is safe to use the image as is from sd-card. Alternatively it is also possible to copy the OS to the internal eMMC for slightly improved performance. Note that the recommended eMMC flasher does not work, but `dd` can be used instead:

```Shell
sudo dd if=/dev/mmcblk0p1 of=/dev/mmcblk1p1
# ⤷ takes 10 - 20 min
```

After the command finishes shut down the Beaglebone either by `sudo shutdown now` or by pushing the button next to the ethernet socket. Remove the sd-card and boot the system back up again. Repeat the tests from above and make sure that the output matches except that `mount` now shows `mmcblk1p1` (eMMC) as root-directory.

For password-less entry & usage of the Beaglebone we prepared an `ansible playbook`. Make sure that you cloned the shepherd-repository locally and installed ansible (compare with general installation-guide from previous section) and also configured the `herd.yaml` in consultation with the full installation guide.

```Shell
# execute in shepherd-repo on host
ansible-playbook ./deploy/setup_pwless_ssh_for_host.yml
```

Now that the Software is ready, a basic test of the shepherd-framework can be run. It is possible to start a pre-configured harvesting demo, even without a cape. This can be done either on the Beaglebone itself:

```Shell
sudo shepherd-sheep run --config /etc/shepherd/example_config_harvest.yaml
```

or on the host by installing and using [shepherd-herd](https://pypi.org/project/shepherd-herd/). After following the linked installation guide the same test can be run with:

```Shell
shepherd-herd start
```

Note that this will load a slightly different configuration-file (`/etc/shepherd/config.yaml`).

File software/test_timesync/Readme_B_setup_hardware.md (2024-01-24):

# Hardware Setup

After [software is ready](Readme_A_prepare_software.md) there are three steps for getting the hardware ready for the measurements:

- get all nodes on the same network
  - Try to model the future network
- route power to each system
  - special reqs. are noted below
  - POE-Adapters are always a good idea
- get the logic analyzer connected to the gpio-trigger-output
  - connecting the ptp server to pin 0 of the analyzer is recommended, as it might show a difference in behavior
  - don't forget to also connect ground

## Quick-HowTo for the Saleae logic analyzer

- channel-numbers are printed on the bottom-side
- the removable connector-leads are color-coded and also have the channel-number printed on the individual ends
- all ground-cables are black & without a channel-number printing

## Raspberry Pi CM4

- power via barrel connector can be 7 - 27 V and defaults to 12 V
- current draw is typically < 150 mA @ 12 V, can increase under load, but is < 500 mA
- signal-pin is the uppermost right on the main connector
- ground reference is right below signal

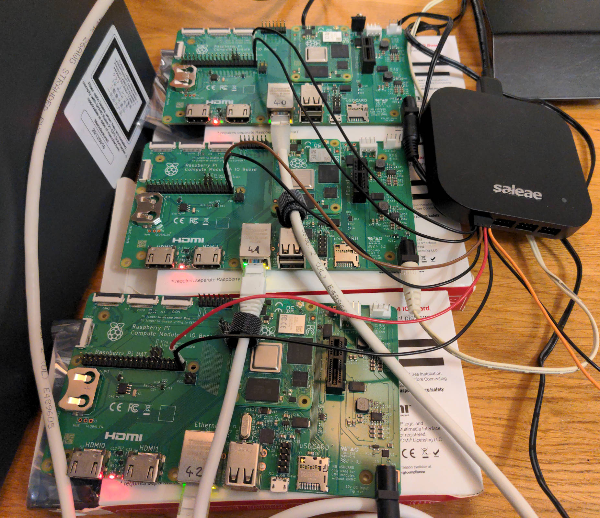
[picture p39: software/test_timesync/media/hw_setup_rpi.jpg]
hw-setup-cm4


## BBone AI64

- power via USB Type C is fine
- be sure to give the heatsink some air - the system can crash from heat
- signal-pin is the second from left on the lower row on P8
- ground reference is left from signal, in the lower left corner

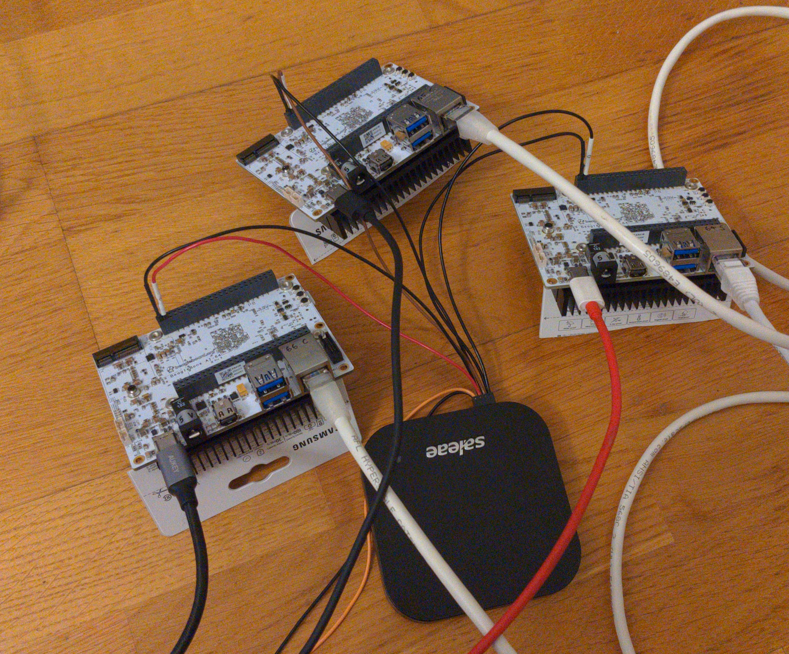
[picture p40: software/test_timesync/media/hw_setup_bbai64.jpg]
hw-setup-bbai64


## BBone Black

Small introduction into beaglebone

- orientation: ICs / CPU visible, ETH-Connector facing left so the white font (silkscreen) on PCB is readable
- there are two large connectors P8 on top, P9 on bottom. each has 46 pins, with pin 1 in the lower left corner - compare with silkscreen
- P8 is our main-connector for the test. Pin 1 & 2 (left-most) are ground / GND
- NOTE: there are (small) white markers on the PCB that indicate start of a decade

Connect logic analyzer to each sheep

- GND goes to P8-01 or P8-02
- Channel wire goes to P8-19 for the kernel-output
- for debug another channel can be hooked up to P8-28 (pru-output)

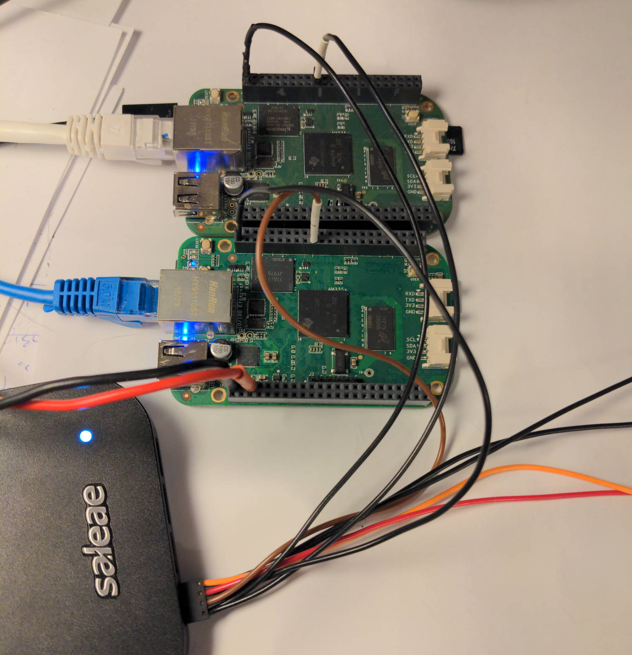
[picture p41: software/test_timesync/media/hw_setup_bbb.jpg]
hw-setup-bbb


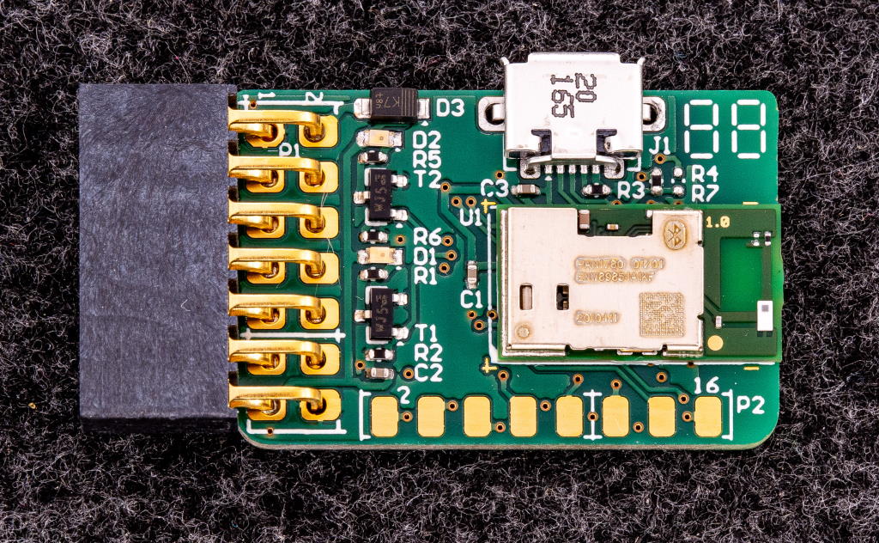
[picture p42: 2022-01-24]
docs/user/pics/pcb_nRF_Target_22_soldered.jpg

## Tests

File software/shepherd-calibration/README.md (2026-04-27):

# Cape-Calibration-Tool

**Main Documentation**: <https://nes-lab.github.io/shepherd>

**Source Code**: <https://github.com/nes-lab/shepherd>

---

`shepherd-cal` is the command line utility for calibrating and profiling a shepherd cape.

## Installation

`shepherd-cal` is a pure python package and currently NOT available on PyPI.

For install from local sources:

```Shell
cd shepherd/software/shepherd-calibration/
pip3 install ./
# or
uv tool install shepherd/software/shepherd-calibration/.[dev] -p 3.12
```

For install directly from GitHub-Sources (here `dev`-branch):

```Shell
 pip install git+https://github.com/nes-lab/shepherd.git@dev#subdirectory=software/shepherd-calibration -U
```

Calibration and profiling **requires a SMU from Keithley**. Our tests and initial calibration are done with a *Keithley 2604B SourceMeter* connected via ethernet. The shepherd-cape must be installed on a beaglebone running the latest shepherd-software and also be accessible via ethernet.

## Usage

The Interface is a semi-stable ATM, so explore the commands on your own:

```Shell
# to see the commands:
shepherd-cal --help
# help for individual commands, ie:
shepherd-cal calibration --help
shepherd-cal calibration measure --help
shepherd-cal profile --help
```

It is currently possible to:

- calibrate the shepherd cape
- read and write calibration to the shepherd cape
- profile the analog frontends (harvester & emulator)
- analyze the profiles with resulting statistics and plots

For actual measurements the program will tell you how to connect the SMU to the cape correctly.

## Examples

### Calibration

```Shell
shepherd-cal calibration measure sheep0 --user jane --smu-ip 10.0.0.24 --cape-serial 1270060 --outfile sheep0_cape_v250e.yaml --verbose
shepherd-cal calibration write sheep0 --user jane --cal-file sheep0_cape_v250e.yaml --verbose
# or new combined measure & write, specialized for the testbed
shepherd-cal calibration measure sheep0 --user jane --smu-ip 10.0.0.24 --emulator-only --write --verbose --cape-serial 20252524
```

### Profiling

```Shell
shepherd-cal profile measure sheep0 --user jane --smu-ip 10.0.0.24 --cape-serial 1270057
shepherd-cal profile analyze ./ --outfile stats.csv --plot
## specialized for the testbed
shepherd-cal profile measure sheep0 --user jane --smu-ip 10.0.0.24 --cape-serial 1270057
```

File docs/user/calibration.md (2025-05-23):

# Calibration

Data recorded with shepherd is stored in the database as raw binary values, read from the ADC.
In order to make sense of that data, we need to map the raw values to physical voltage and current values.
Similarly, for emulation, we need to map physical voltage and current values to binary values that can be fed to the DAC.

This mapping is assumed to be linear.
For example, to convert a raw value :math:`v_{raw}` to its physical equivalent :math:`v_{physical}`:

```{math}
v_{physical} = v_{binary} \cdot gain + offset
```

There are two "channels" and two "variables": harvesting and emulation, each with voltage and current.
When storing recorded data, these values are stored together with the raw data.

The *gain* and *offset* values can be derived from nominal hardware configuration.
However, due to component tolerances, offset voltages and other effects, the real mapping can significantly differ from nominal values.

Therefore, we recommend to *calibrate* shepherd by comparing a number of sample points recorded with shepherd to known reference values measured with accurate lab equipment.
From the tuples of reference values and measurements, you can estimate the *gain* and *offset* by ordinary least squares linear regression.
These values can be stored in the EEPROM on the shepherd cape and, at the beginning of a recording extracted and stored in the database file.

## References

- [data-models in user-tools](https://github.com/nes-lab/shepherd-tools/blob/main/shepherd_core/shepherd_core/data_models/base/calibration.py)
- [cal-tool-documentation](../external/readme_cal.md)

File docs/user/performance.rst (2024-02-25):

Performance Specification
=========================

The `Performance specification`_ table summarizes shepherd's key performance metrics.
Refer to our paper for a detailed description of how these values were obtained.
Some of the values were measured with an early prototype and may not accurately reflect the current hardware revision.

.. table:: Performance specification

    +----------------------------+------------------------+----------------------+
    | Range                      | Harvester voltage      | 0 mV - 4.8 V         |
    +                            +------------------------+----------------------+
    |                            | Harvester current      | 0 mA - 50 mA         |
    +                            +------------------------+----------------------+
    |                            | Emulator voltage       | 0 mV - 4.8 V         |
    +                            +------------------------+----------------------+
    |                            | Emulator current       | 0 mA - 50 mA         |
    +----------------------------+------------------------+----------------------+
    | 24h DC Accuracy            | Harvester voltage      | 19.53 uV +/- 0.01 %  |
    +                            +------------------------+----------------------+
    |                            | Harvester current      | 190 nA +/- 0.07 %    |
    +                            +------------------------+----------------------+
    |                            | Emulator voltage       | 76.3 uV +/- 0.012 %  |
    +                            +------------------------+----------------------+
    |                            | Emulator current       | 381.4 uA +/- 0.025 % |
    +----------------------------+------------------------+----------------------+
    | Bandwidth                  | All recording channels | 15 kHz               |
    +----------------------------+------------------------+----------------------+
    | Risetime                   | Emulator voltage       | 7 us                 |
    +                            +------------------------+----------------------+
    |                            | Emulator current       | 19.2 us (?)          |
    +----------------------------+------------------------+----------------------+
    | GPIO sampling speed        |                        | 580 kHz - 5 MHz      |
    +----------------------------+------------------------+----------------------+
    | Power consumption          |                        | 345 mA               |
    +----------------------------+------------------------+----------------------+
    | Max. Synchronization error |                        | < 1.0 us             |
    +----------------------------+------------------------+----------------------+

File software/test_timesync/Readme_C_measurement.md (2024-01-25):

# Measurement

## Preparation

- set up hardware according to the [tutorial](Readme_B_setup_hardware.md)
- check that ptp is working
  - option 1: via logic analyzer (see subchapter below)
  - option 2: via ssh-connection (commands below)
- PTP should be given >= 5 minutes to stabilize
- room-temperature should be stable, as clock-crystals react to that

**Note for RPi CM4**

Changing the governor does not always work during boot, please check. At least the ptp-server is mostly stuck on `ondemand`.

```Shell
# check
cpufreq-info
# reset
sudo cpufreq-set --governor performance
```

### Quick-HowTo for Sync-Services

Current state of PTP can be checked on the nodes with

```Shell
sudo journalctl -u ptp4l@eth0.service -b -f
sudo journalctl -u phc2sys@eth0.service -b -f
```

Fixing time-sync problems can be solved be restarting the services and shepherd-kernel-module

```shell
# note: if ptp is restarted, phc must also be restarted
sudo systemctl restart ptp4l@eth0
sudo systemctl restart phc2sys@eth0
```

Screenshots of correctly running [ptp](media/ptp_running_fine.png) and [phc2sys](media/phc2sys_running_fine.png) services are show behind the link. Both tools can misbehave when other ptp-hosts are present. Frequency adjustment value usually jumps to max in that case (+-100 us).

### Quick-HowTo for Logic 2 Software

- config under `Device Settings` (device-shaped symbol in top left corner of plot)
  - select connected channels -> usually `0 to 2` (Digital, NOT Analog)
  - select highest samplerate -> `500 MS/s`
  - select highest voltage-levels -> `3.3+ Volts`
  - set `Timer` to record for `100 s` (and stop automatically after that)

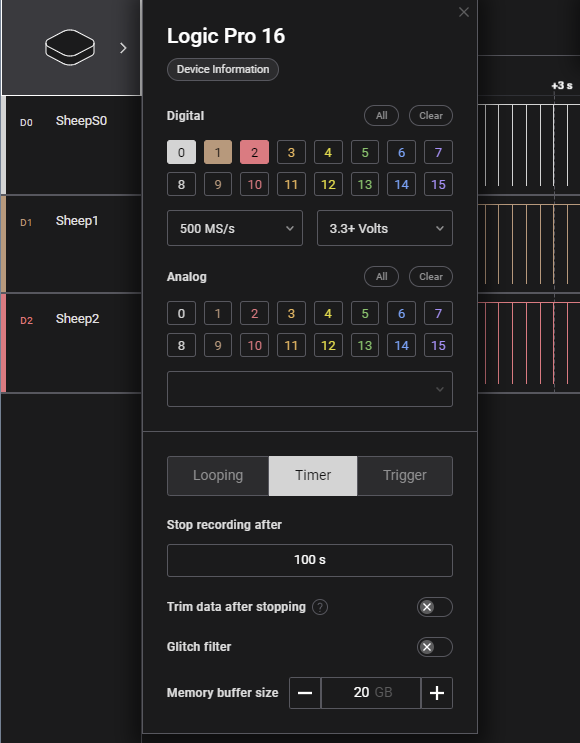
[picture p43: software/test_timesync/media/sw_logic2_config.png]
Logic2-config


- a failed sync looks like that:

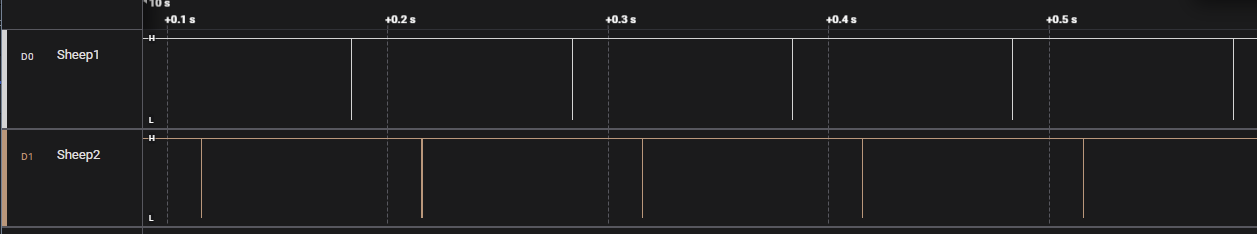
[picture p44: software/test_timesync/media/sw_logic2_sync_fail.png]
Sync-Fail


- a successful sync shows minimal delay between the rising edges of each node, seen here with 92 ns as largest distance

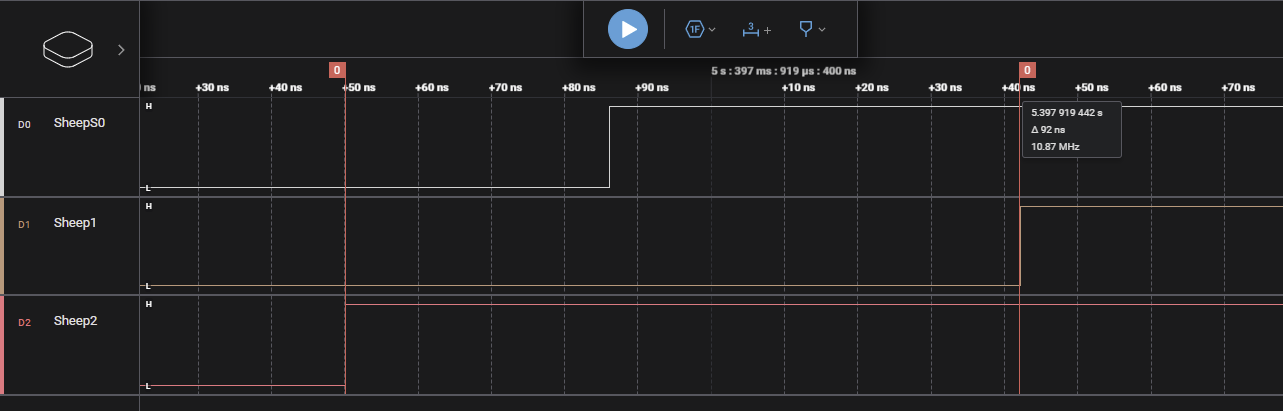
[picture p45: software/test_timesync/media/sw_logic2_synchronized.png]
Sync-Fail


**Don't forget** to save the capture after each measurement with a meaningful name, i.e. `01_baseline.sal`!

### Quick-HowTo for IPerf3

IPerf3 can be used to generate network traffic.

```Shell
sudo apt install iperf3

# mockup server: device receiving data
iperf3 -s

# ptp-clients send, here 100Mbit to server-IP for 10 s
iperf3 -b 100M -c 10.0.0.200
```

The server can only receive data from one client at the same time. Therefore the two ptp-clients should be used in alternating pattern. It's best to start the recording first, then begin with traffic and alternate for ~ 50 - 70 s. The recording should show ~ 20 s of ptp getting back to normal at the end.

## Collecting the Data with Logic 2 Software

It's recommended to separate different campaigns and hardware-setups by subdirectories. A small textual description can help for later analysis. Notes of oddities and reported ptp path delays add valuable context.

The following measurements are recommended:

- 01 - baseline (stable, undisturbed network)
- 02 - ptp-clients send data to external host with 100 Mbit/s
- 03 - ptp-clients send data with 200 Mbit/s
- 04 - ptp-clients send data with 400 Mbit/s
- 05 - ptp-clients send data with 800 Mbit/s
- 06 - ptp-clients receive data from external host with 100 Mbit/s
- 07 - ptp-clients receive data with 200 Mbit/s
- 08 - two external hosts send at max rate

Each running for 100 s.

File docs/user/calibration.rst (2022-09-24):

Calibration
===========

Data recorded with shepherd are stored in the database as raw binary values, read from the ADC.
In order to make sense of that data, we need to map the binary values to physical voltage and current values.
Similarly, for emulation, we need to map physical voltage and current values to binary values that can be fed to the DAC.

This mapping is assumed to be linear.
For example, to convert a binary value :math:`v_{binary}` to its physical equivalent :math:`v_{physical}`:

.. math::

    v_{physical} = v_{binary} \cdot gain + offset

There are two "channels" and two "variables": harvesting and emulation, each with voltage and current.
Thus the complete set of calibration values consists of 12 values.
When storing recorded data, these values are stored together with the binary data.

The *gain* and *offset* values can be derived from nominal hardware configuration.
However, due to component tolerances, offset voltages and other effects, the real mapping can significantly differ from nominal values.

Therefore, we recommend to *calibrate* shepherd by comparing a number of sample points recorded with shepherd to known reference values measured with accurate lab equipment.
From the tuples of reference values and measurements, you can estimate the *gain* and *offset* by ordinary least squares linear regression.
These values can be stored in the EEPROM on the shepherd cape and, at the beginning of a recording extracted and stored in the database file.

Support for an automated calibration procedure with *shepherd-herd* will be added soon.

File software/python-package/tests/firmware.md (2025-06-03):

# Firmwares

## Usage

```Bash
	sudo shepherd-sheep -v program --mcu-port 1 --mcu-type nrf52  firmware_nrf52_testable.hex
	sudo shepherd-sheep -v program --mcu-port 2 --mcu-type msp430 firmware_msp430_testable.hex
	sudo shepherd-sheep target-power
	# alternatively run with "-p B" for the second target port
```

## firmware_nrf52_powered.hex

The app monitors up to eight GPIO pins for rising edges and upon detection prints the index of the pin where the edge was detected over UART. Simultaneously, it waits for incoming messages on the UART. When receiving an ASCII encoded number between 0 and the number of configured pins, the app sets the corresponding pin high for ~100us.

Edit the `pins` array and the UART pin definitions at the top of `src/main.c` to reflect your hardware.

### Functionality

- LEDs
	- blink / switch 10x at startup
	- 50 / 150 ms
	- P0_13, _14 (Target v2.1)
- UART
	- P0_06 TX, _08 RX (Target v2.1, SDK)
	- listens and answers
	- should answer when GPIOs are triggered
- GPIO
	- active: P0_20 - P0_25 (GPIO 0 to 5)
	- switch on for 100 us after receiving on UART ("(%u)\r\n")

[Source](https://github.com/nes-lab/shepherd-targets/tree/main/firmware/nrf52_testable)

## firmware_msp52_testable.hex

The firmware toggles all 3 LEDs 16 times for 100 ms and does the same for the 10 external GPIO (4 times).

### Functionality

- LEDs
    - blink / switch on 16x at startup
    - 100 ms on / 100 ms off
- GPIO
    - active: P0_20 - P0_25 (GPIO 0 to 5)
    - switch on for 100 us after receiving on UART ("(%u)\r\n")

[Source](https://github.com/nes-lab/shepherd-targets/tree/main/firmware/msp430_testable)

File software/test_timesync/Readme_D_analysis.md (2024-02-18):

# Prepare Data for the Tool

- Logic 2 Software -> File -> Export Data
- select channels: 1-3
- Time Range: All Time
- Format: CSV
- DON'T use ISO8601 timestamps
- Export and rename file to meaningful description

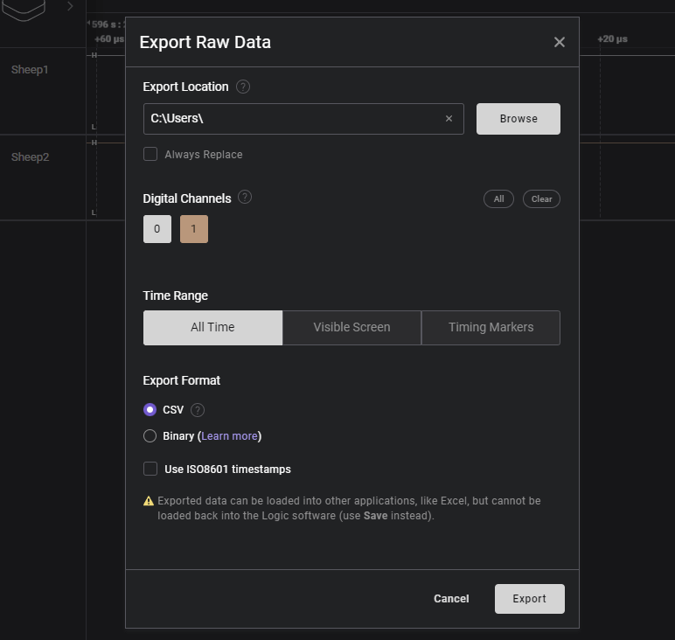
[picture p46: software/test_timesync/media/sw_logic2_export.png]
logic_export


# Analysis

Setup:

- same cisco switch
- same software configuration (where possible)
- data recorded with a Logic Pro 16 @ 500 MHz
- nodes & network are at rest (baseline)

## GPIO - Jitter

How accurate is the 100 ms trigger on different platforms? Let's visualize the jitter of one node.

In numbers:
- simplified
- `Δ_q1 = 99%-Quantile - 1%-Quantile`
- `Δ_max = Max - Min`

| name                              | Δ_q1 [ns] | Δ_max [ns] |
|-----------------------------------|-----------|------------|
| BBB_023_ABS_HARD_ch0_rising_100ms | 874       | 1050       |
| BBAI_02_ptp_piservo_[..]ing_100ms | 464       | 16552      |
| 010_cm4_baseline_ch0_rising_100ms | 78        | 286        |

**BBone Black**

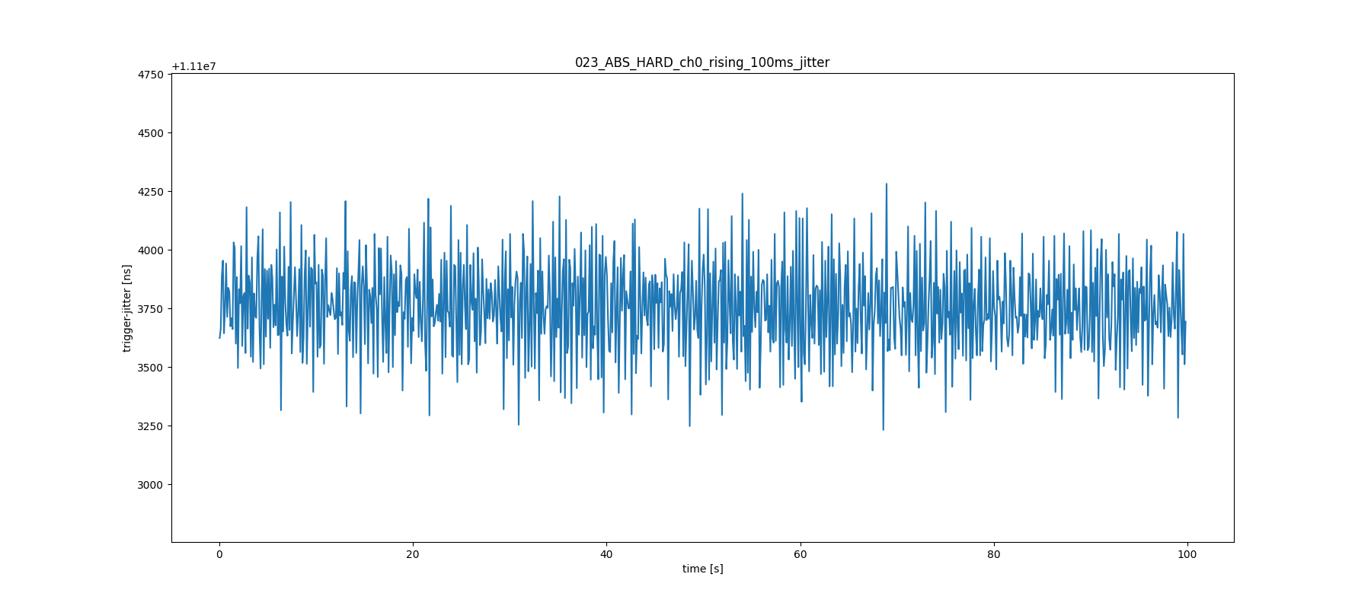
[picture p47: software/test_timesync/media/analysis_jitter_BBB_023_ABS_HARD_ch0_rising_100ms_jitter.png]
GPIO-Jitter-BBB


**BBone AI64**

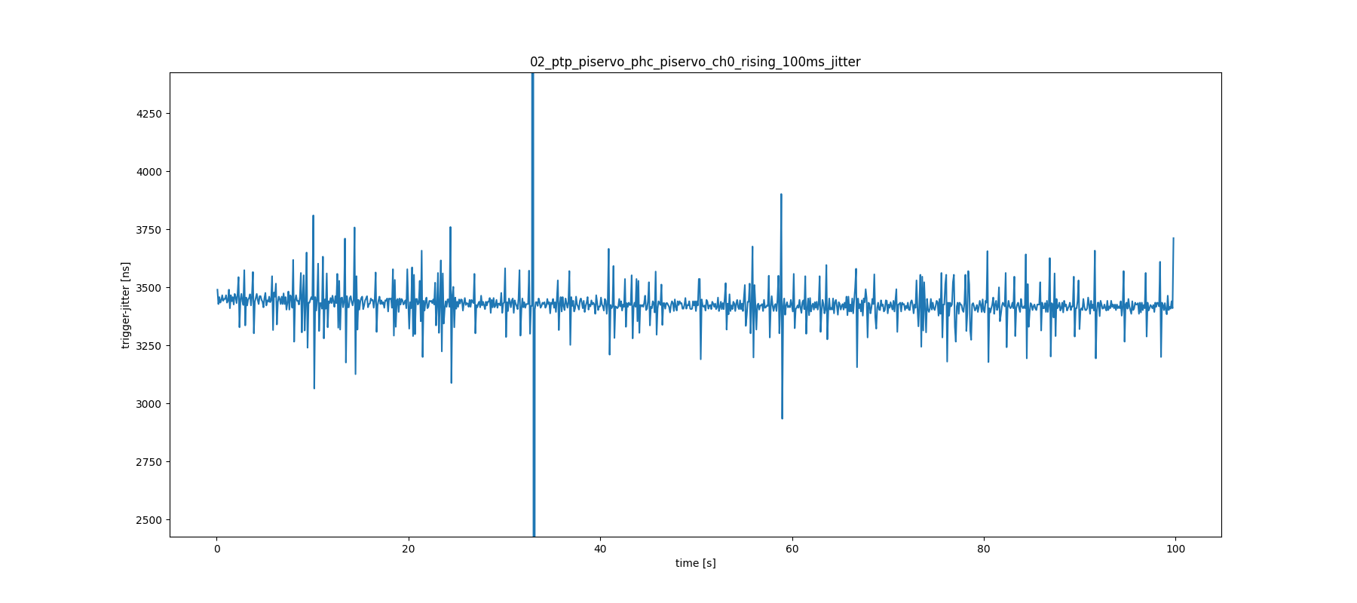
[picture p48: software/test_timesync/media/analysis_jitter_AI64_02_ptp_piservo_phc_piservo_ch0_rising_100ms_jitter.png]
GPIO-Jitter-BBAI


**Raspberry Pi CM4**

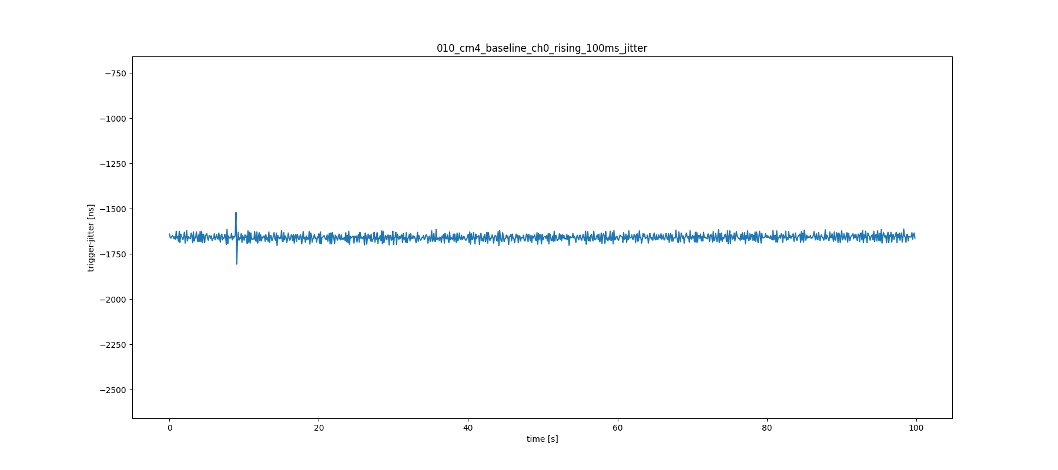
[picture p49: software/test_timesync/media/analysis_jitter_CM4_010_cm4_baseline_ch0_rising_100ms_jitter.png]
GPIO-Jitter-RPiCM4


Some context and final words:
- BBB takes ~ 300 ns to get kernel time. performance looks fine considering the age of the platform
- BBAI takes ~ 40 ns to get kernel time. the random spikes are still unexplained. It could be caused by register-write-locks. The SOC has several coprocessors that share the same bus (linux shows 2ß rProc). Also the system is missing a RT-Kernel.
- CM4 was overclocked to match BB-Ai, so it also takes ~ 40 ns to get kernel time. jitter looks best of these three systems

## Sync Performance

In numbers:
- `Δ_q1 = 99%-Quantile - 1%-Quantile`
- `Δ_max = Max - Min`

| name                         | Δ_q1 [ns] | Δ_max [ns] |
|------------------------------|-----------|------------|
| BBAI_02_ptp_piservo_[..]_1u2 | 669       | 1182       |
| RPI_005_norm_80_70_diff_1u2  | 336       | 378        |

**BBone AI64**

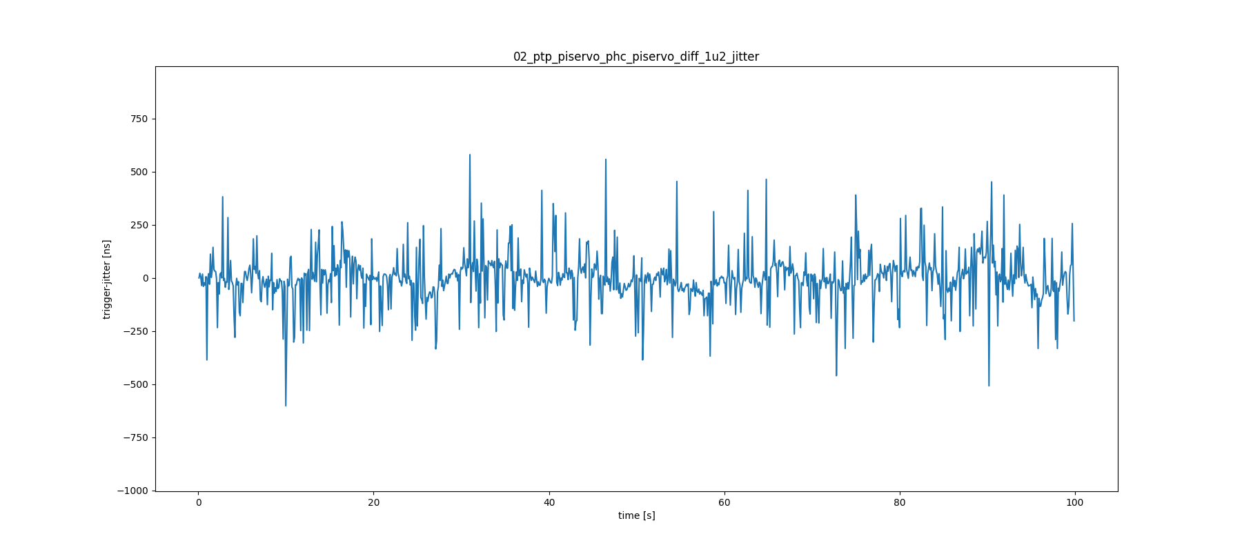
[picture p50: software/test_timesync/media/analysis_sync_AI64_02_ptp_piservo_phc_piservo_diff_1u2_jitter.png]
Sync-BBAI


**Raspberry Pi CM4**

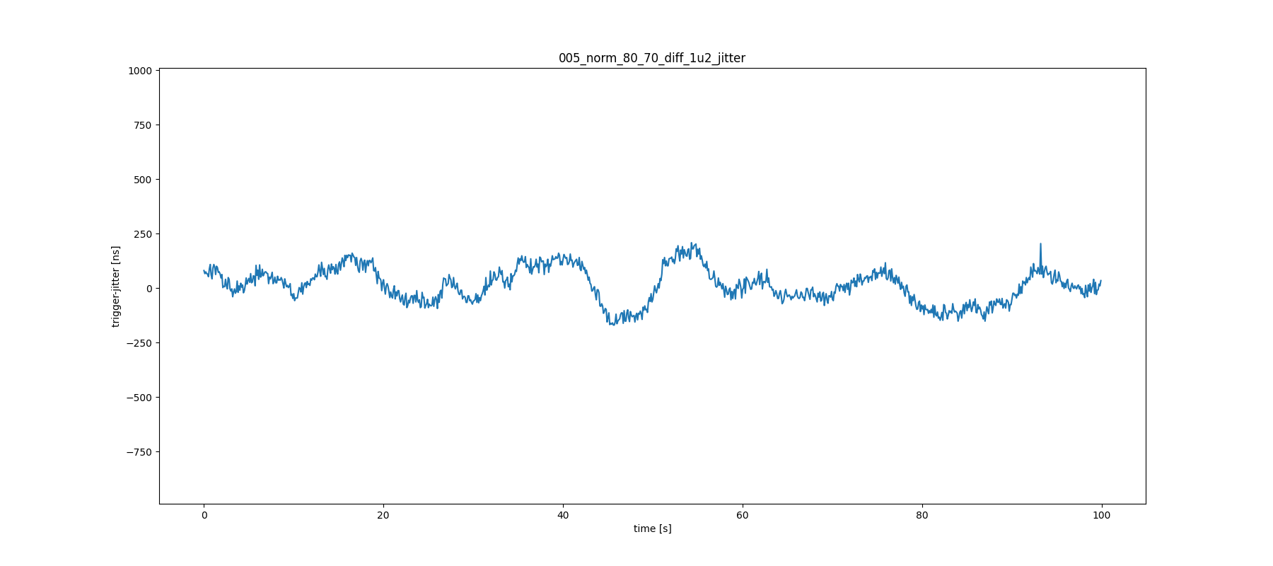
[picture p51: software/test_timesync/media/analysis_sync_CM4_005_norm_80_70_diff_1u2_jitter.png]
Sync-RPiCM4


## Deeper Dive

Raw data and Plots are at [shepherd-planning](https://github.com/orgua/shepherd_v2_planning/tree/main/timesync'24)

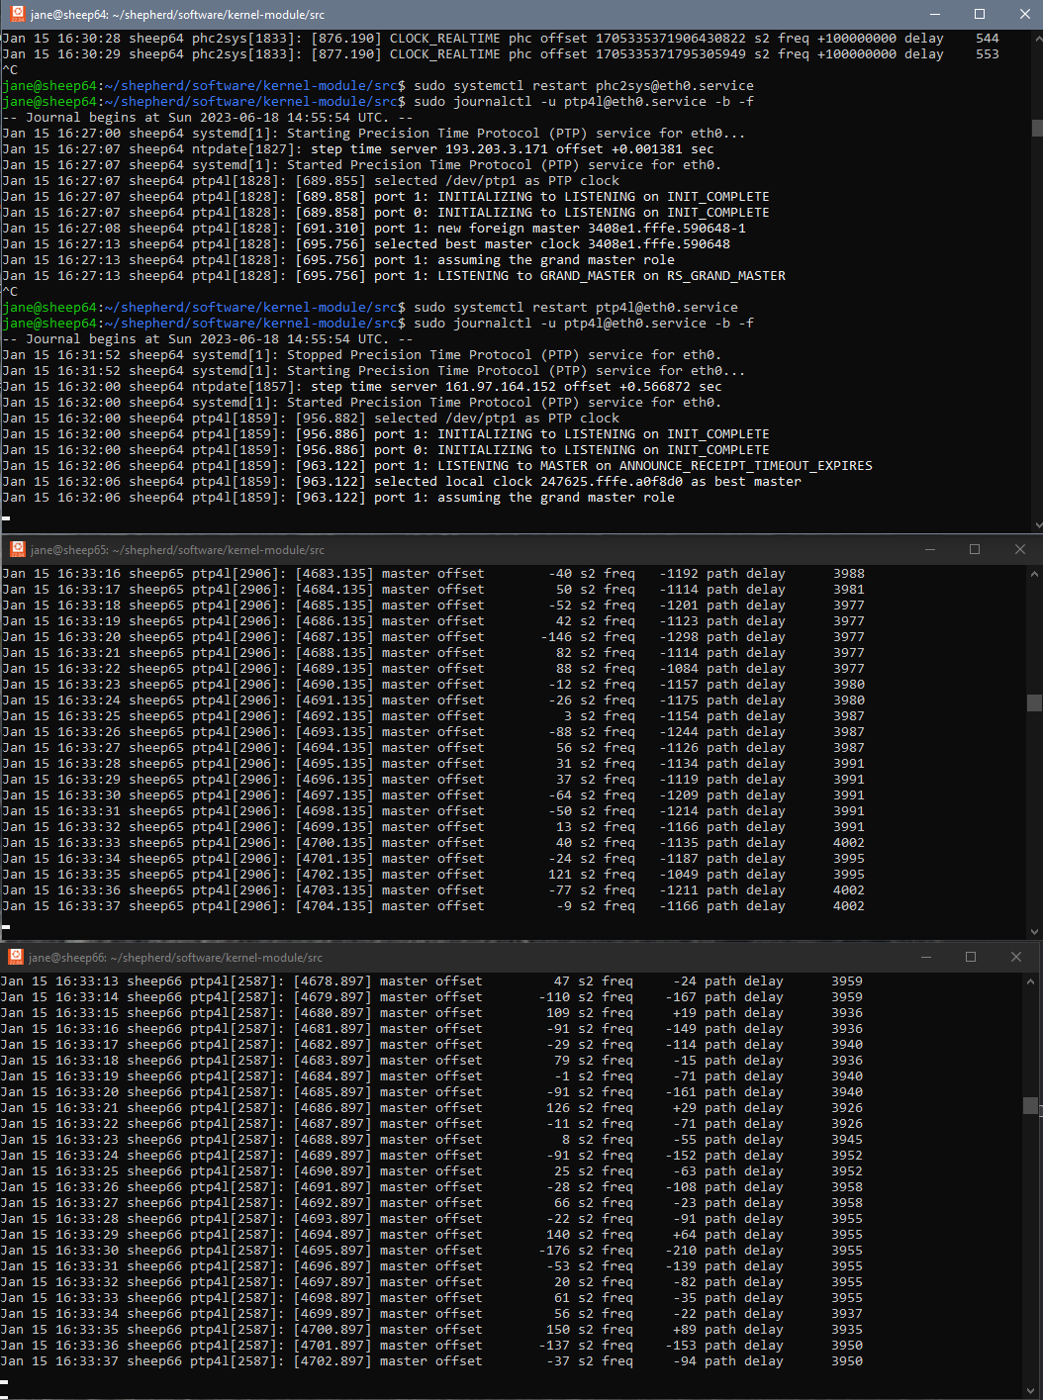
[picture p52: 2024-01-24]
docs/dev/time_sync_measurement/ptp_running_fine.png

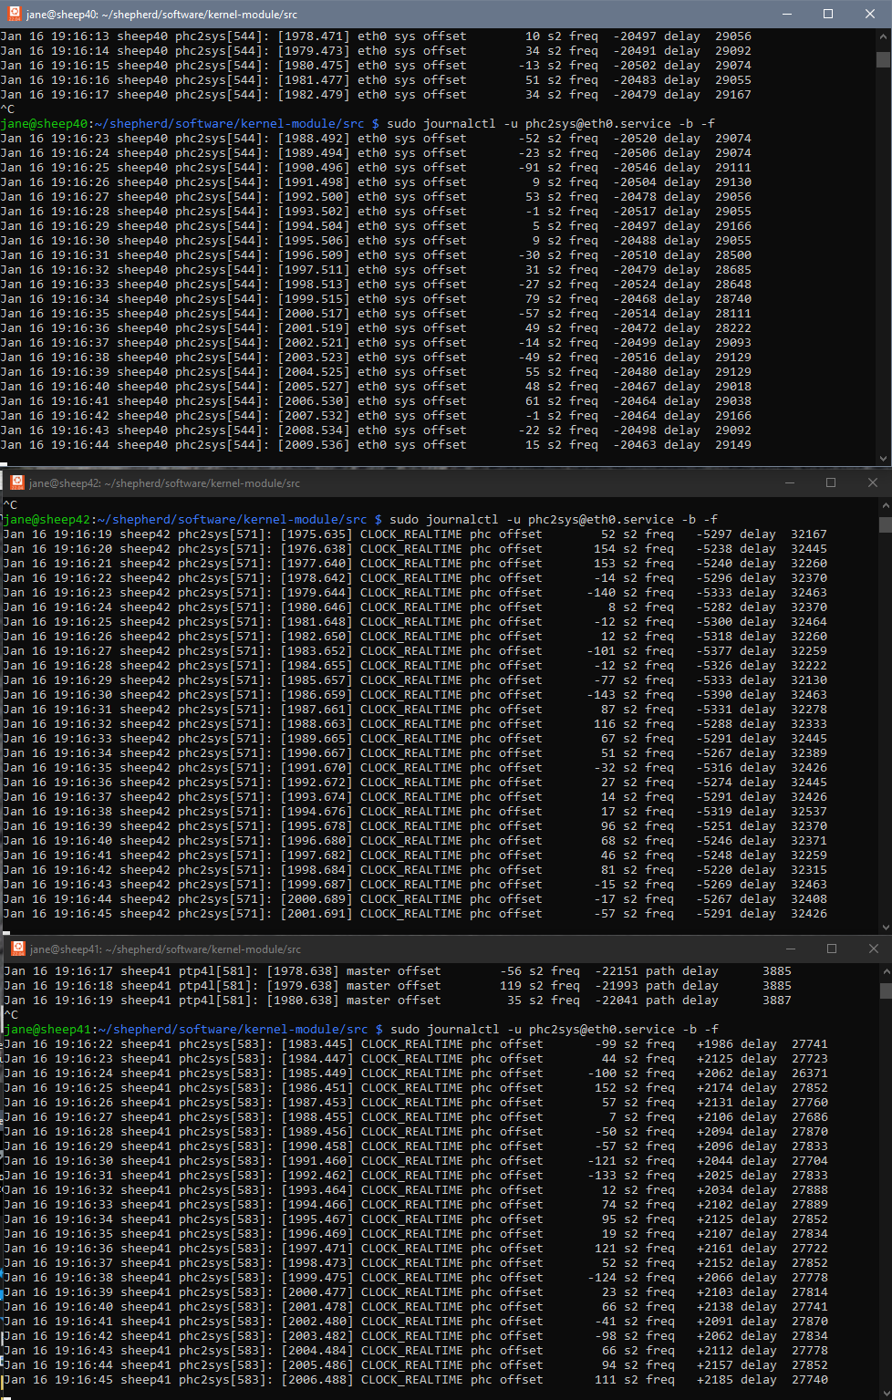
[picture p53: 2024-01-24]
docs/dev/time_sync_measurement/phc2sys_running_fine.png

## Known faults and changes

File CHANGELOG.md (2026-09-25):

# History of Changes

## 2026.09.1 - unreleased

Sheep
- improve performance of Hdf5-Writer by adding shuffle and optimizing chunking of timeseries
- fix shared-mem access (potential bug)
- add & update performance-benchmarks

Watchdog
- add tooling to automatically update the hostname. This is helpful when swapping SD-Cards of the observers as this was the last manual update step. The hostname is derived from the MAC address. This will only work if the MAC address is found in the observer-fixtures of the testbed-client.
- make system immune to faulty config (avoids exception-loop with high cpu-util)

Herd
- add forced reboot via sysrq (CLI `unstick`). SYSRQD_KEY must be present in env-variables
- make .open() less demanding

Ansible
- cleaning-role
  - keep shepherd/.git dir
  - remove more packages
  - speed up package-removal
- harden_fs - remove new swap, improve root-detection
- maintenance-role - integrate harden_fs
- observer-role
  - allow adding datastorage without connection
  - grow root-partition/FS (disabled for now)
- general speedup by using new config-options (fact caching, skipping compression, keeping ssh-connections)
- improve sshd-stability
- ptp-host-role
  - revert to use included PTP
  - try normal hw-filtering
  - disable PTP-compiling and reload systemd after setup
- image-acquire-script is faster and reports errors
- add playbook for updating kernel (for testbed usage)

Kernel-Update 6.1 - Main Improvements:
- switch from 4.19.94-ti-r74 (2018-10) to 6.1.83-ti-r39 (2022-12)
- simplify device-tree (downward compatible)
- makefile for device-tree compiles & installs all possible variations
- generalize GPIO-usage via sysfs (downward compatible) as gpiochip# is initialized async and order can change on newer kernel versions
  - gpio-access via sysfs is now ready for kernel 6.1 to 6.18 (tested)
- migrate to newer kernel API
- heavily improve safety of kMods init-phase & shutdown
- migrate to newer pru support package (5.9 to 6.5) with different style of reserving interrupts
- resolve issue with OCMC-RAM that is used by shepherd-cache and power-management

Kernel-Update 6.1 - Downsides:
- OCMC-Cache between System and PRU is only half from before (it's partly used by linux)
   - from 64 kByte or 82 ms buffer to 32 kByte or 41 ms
   - power management (PM) uses the first 8 kByte, but cache-design needs 2^n
   - PM could be turned off (runtime-command available), but no one guarantees, that the OCMC isn't written to -> one could try to modify the device tree and NOT reserve that 4+4 kByte and check if system sticks to it (using shepherd resulted in a kernel panic when that shared area was modified)

Kernel-Update 6.18:
- migrate from 6.1.83-ti-r39 (2022-12) to 6.18.53-bone55 (2025-11)
- that's the first kernel-version that fully supports the beaglebone green eco
- device-tree - build-process now uses provided includes (less custom, error-prone code)
- read/write-performance seems to have improved ~ 10 %
- add back benchmark for ktimers

Misc
- add custom compiled PTP
- update cape-errata, h5-benchmark
- sheep - fix exception during end of resync

Speed-Benchmark on a Beaglebone Green (compiled from [testbench_direct_rw](https://github.com/nes-lab/shepherd/blob/main/software/python-package/tests_manual/testbench_direct_rw_results.md)):

| type          | static (60s R/W) | random (60s R/W) |
|---------------|------------------|------------------|
| none-base     | 2.970 / 11.593 s | 2.988 / 10.646 s |
| lzf-base      | 4.024 / 17.988 s | 3.588 / 26.893 s |
| gzip1-base    | 5.960 / 21.154 s | 6.777 / 29.791 s |
| none-shuffle  | 3.882 / 12.330 s | 3.886 / 11.226 s |
| lzf-shuffle   | 3.994 / 10.913 s | 4.231 / 20.715 s |
| gzip1-shuffle | 4.901 / 12.583 s | 5.932 / 22.650 s |
| gzip6-shuffle | 4.947 / 14.875 s | 5.847 / 24.561 s |

## 2026.07.1

Sheep
- emu - exit measurement loop when PRU switches to idle
- emu & hrv - exit non-zero if an error (or worse) was handed to logger during measurements
- emu & hrv - force small 1 or 10 ms breaks in main loop (depending of workload)
- emu - fix high CPU load during last 10 s of measurement (small chunks were activated too early)
- emu - properly exit main-loop when faulty condition is detected
- monitors - add backlog as argument
- monitors - add raw logs for ptp & phc2sys
- monitors - give more time to quit and just warn if that fails
- remove host-name and process-id from monitors
- gpio-recorder - decrease chunk-size from 1 MiB to 500 kiB (even out cpu-load)
- resync CLI-option now waits for PTP to settle (with custom timeout)
  - herd now uses that exact function from sheep
- mount CLI-option now reconnects and checks availability of network drives

Programmer - SBW / msp430
- add forced mode, that ignores errors during device.open()
- inform via CLI, that data-rate option is ignored (SBW has fixed speeds)

PTP - tune to be less susceptible to high CPU load
- increase prios and change scheduler of ptp-kworker, ptp, phc2sys
- increase timeout for answer of kworker (PTP tends to jump)
- increase prios of socket and dscp type (QoS)
- set clients to "clientOnly 1" (this needs a dedicated timeserver)
- prioritize clock of server setting priority1, clockAccuracy, ClockClass to make it a (fake) GM
- sync GM of server via NTP / chrony
- ~~bump prios of all kworkers and network-service~~
- ~~activate filter for hw-timestamping~~

Misc
- herd - log-fetching differentiates active from failed instances (exit-code -1)
- all CLI-tools exit non-zero when receiving external signal
- herd - resync-cmd uses implementation of sheep
- herd - added mount-cmd, uses implementation of sheep

## 2026.06.2

Make the root filesystem less prone to errors

- added playbook `dev_harden_rootfs.yml`
- strategy 1 - move temporary data from FS to RAM
- strategy 2 - make mounting of root-filesystem more robust
- strategy 3 - check filesystem on every boot
  - this caused the kMod to NOT start up, because PRU0 could not load firmware, because allocation of buffers in DRAM failed
  - 3 possible fixes were tried (https://github.com/nes-lab/shepherd/issues/162), all failed
  - ~~migration to a newer kernel is recommended~~
  - **increasing Contiguous Memory allocation (CMA) in u-boot from 50M (default) to 200M solved the issue**

Programmer

- OpenOCD now works with v2 capes and is able to program, mass-erase and chip-erase the nRF52 (and probably all other supported targets)
  - this will replace the limited pru-programmer

KMod - fix sporadically failing start of module

- increasing CMA (see above) fixed the issue of a sometimes failing load of the module due to a failed allocation
- PRU0-firmware requests ~47M of RAM, which was dodgy for a 50M default value
- benchmarks show no degradation over 400 loads. mean-time = min time = 390 ms (before it needed ~40 s sporadically)
- available cma can be checked with `cat /proc/meminfo | grep Cma`

Other Changes

- kModule informs about buffer-specs in DRAM (address & size)
  - also tests size of buffers it can see
- ansible: add internet-watchdog to observer-role -> in addition to dedicated watchdog IC, which restarts system when reset-pin is not constantly polled, this internet-watchdog checks access to remote IP addresses and restarts system if the network is down

## 2026.06.1

PRU-Programmer got the same reliability-booster as emulation & harvester

- PRU logs that settings were applied
- python checks if config was written correctly to PRU-memory
- python checks if PRU applied settings
- note that the programmer got more reliable with the last release as well -> forced pru-resets are not occasionally discarded

Sheep

- cleaner exit on already misbehaving sheep-routines
- ID-patching now informs if it skips due to wrong file-format
- shorten programmer error-count before failing -> gives more time for retries

KMod - fixed leakage of Pru-handles during loading and unloading of module

- when PRUs were not fully ready during boot, references were lost in several places
- during removal, the references were not returned at all
- code was made much safer by handling all possible code-paths (proper cleanup)
- test with `sudo lsmod | grep pru_rproc` before and after `sudo python3 python-package/tests_manual/testbench_kernelmodule.py`
  - reference count of sub-modules is correct and does not increase during usage

## 2026.05.1

Sheep

- improve handling of kernel module - this prevents an endless reload-loop
- prevent early exit if power-tracing is disabled (10 s missing)
- ~~transform pru_util into a monitor-thread to prevent overfilling buffer during waiting~~
  - bad idea as a non-atomic monitor-thread corrupts shared-memory-access
  - better: add pre-experiment-loop that collects pru-util data
- add pre-experiment loop that collects pru-util data (avoids warning to user)
- sheep - read back and verify written settings in pru-memory (now default for emu & hrv)
- verify that settings where actually applied in PRU before starting a measurement (wasn't fully done for hrv)
- virtual harvester - ivsurface recorder - add fixed-length and automatic cutout-mode
  - the config-model got new parameters and the firmware is respecting them
  - documentation can be found here: https://github.com/nes-lab/shepherd/blob/main/docs/user/virtual_harvester.md#ivsurface---transition-cutout

KModule

- allow reading and resetting pru-applied-settings-flag
- bugfix - forced PRU-reset could be discarded before

Watchdog

- add network-checker that pings 5 internet-hosts and reboots after all failed
  - feature is turned off per default as it can misbehave in harvesting-scenarios without internet access
- config is located @ `/etc/shepherd/watchdog.yaml`

Ansible

- install / build rYAML separately from install sheep

Github

- compile PRU-firmware with GCC 16.1, gnupru 2026.05

## 2026.04.2

This update brings performance improvements, fewer bugs and removes limitations that are problematic for additional future testbeds.

**Breaking Changes:** The whole shepherd-software-stack will have to be updated.

### Highlights

- execution time of VSrc on PRU significantly reduced by > 20%
- increased resolution and range of LUT-division for VSrc in PRU
- use more safe math FNs in vsource code (now, that there is room)
- fix wrong cal being used when tracing energy storage
- add support for new cape hardware v2.5e (more target IO, two power good pins)
  - the altered wiring frees up PRU1 - so idle GPIO sampling improves by 20 % (from 1.4 to 1.67 MHz)
- power-good is now calculated with two pins in mind (low & high threshold) and automatically falls back to hysteresis if second pin is missing in hardware (capes before v2.5)
- massive speedup of sheep-tool, see https://github.com/nes-lab/shepherd/issues/150 for benchmarks
  - big refactoring or core-lib and cli.py to avoid expensive imports
  - replace PyYAML with faster ryaml

### Details

Sheep

- fix for a fix #133 - tracing intermediate voltage now works as expected
- move from setuptools to uv
- unittests - limit tests to capabilities of cape (hrv, emu)
- CLI - add `resync`
- ~~increase warning for pru0-util from 95 % to 98 %~~ (reverted for early warning of overload)

PRU

- fix wrong cal being written to PRU when tracing energy storage
- optimize LUT-division to cover 0.13 to 16 V and be more precise and less compute-heavy
  - add python script for calculation and visualization
- add special mul32e() to allow full expansion u32*u32 = u64
- optimize VSrc in PRU0 to use less u64-calculations
  - utilization drops from 96 % mean, 99 % max with a heavy config to 75 % / 78 %
  - fixes #123
- use more safe math FNs in vsource code
- internal refactoring & renaming mostly around BATOK (now called power good)
- activate `-Wpedantic` for py-module / c-code and fix warnings
- activate `-Wpedantic` for pru-firmwares / c-code ~~and fix warnings~~
- PRU0 - add error when gpio-trace result won't fit into current buffer-design

Support for new cape hw v25

- split & add device-tree to support both capes
- add cape-abstraction to PRU, sheep, ansible
- test both cape versions in GH workflows
- add `CAPE_HW_VER` to build-systems for altering config
  - `shepherd-sheep eeprom read --hw-version` now returns that version (i.e. prints `25` on screen)
- power good is now calculated with two pins in mind (low & high threshold)
  - it is automatically translated to hysteresis if second pin is missing
  - for cape v2.5 it will be set on PRU0, making room for slightly higher GPIO-tracing rates
- PRU0 - disable LED-DEBUGGING as all available pins are used for IO on cape 2.5 (will also make GPIO-Tracing faster)
- the new cape has a different wiring - the PRU1 sampling GPIO has less maintenance to do
  - so the worst execution time resulted in 1.4 MHz idle sampling before
  - the new cape is able to sample at 1.67 MHz (minimum, idle) -> 20 % improvement

Misc

- python-tools
  - modernize codebase
  - switch from utf-8-sig to plain utf-8
- py / uv - abandon global cache
- ansible
  - improve uv commands
  - make scripts compatible with new cape
  - repair and tune functionality
  - extend cleanup before image-generation
  - add config for journald, to limit storage usage
  - tweak renaming of hostnames
- documentation
  - improve information about compatible linux distros
  - add info about how to set up a read-to-use linux-image
  - add info about how to switch software to another cape-versions
- internal - move doc for the release-procedure to root readme
- hardware
  - add case for observer
  - add test-routine for new capes
  - update testbed information-sticker
  - add cage for cape
  - add bulk holders for up to 5x cape and 10x target PCBs (can be configured via OpenSCAD)
  - add cable clip 3d-file
  - revert deprecation of cape v2.4c, as it is essential for harvesting
- herd - add timediff-command
- cal-tool
  - add plotting-script to show multiple cal
  - add CLI-command to plot a cal
- add zizmor to find vulnerabilities in GH actions
  - explicitly clear permissions of GH-actions and reduce elevation-surface
- **tested**: ansible install, pytest sheep, pytest herd windows, ~~pytest shepherd_pru~~ unchanged

## 2026.02.1

- project changes to stable and adjusts version-format to `YYYY.MM.r` (year, month, release-number)
- this release needs core-lib >= 2026.02.1 due to new features
- new virtual battery (generalized energy storage for vsource)
  - pru-firmware (c-code) got port of python-model
  - models and parametrization were evaluated in core-lib
  - added [documentation for storage](https://nes-lab.github.io/shepherd/user/virtual_storage.html)
  - update python pru-module (sim interface to c-code)
  - extend testing of custom math functions (c-code)
  - make storage configurable via kernel-module and sheep-package
  - added [performance analysis](https://github.com/nes-lab/shepherd/blob/main/software/debug_compare_vsources/README.md) that documents harvesting and emulation results (python models vs. c-code vs. emulation by pru-firmware)
- sheep
  - ~~won't exit with != 0 if config is not for that specific sheep~~
  - improve and bugfix resampling of output-data (also direct power-calculation) -> numpy brings beaglebone to a halt on vector-float-operations during measurement
  - add benchmark to find the cheapest resampling method
  - fix csv-header for pru-util
  - use ExitStack() more correctly
  - speed up & stabilize reload of kernel module
    - factor 8, later ~ x12, so from 8 to 45 s down to .7 s
    - this shaves 20 min off unittests and makes them run through again
  - disable changing fw of Pru1 (gets now automatically selected, based on fw for pru0)
  - improve warning of watchdog for possible fifo-overflows (more explaining, less scary)
  - use correct scaling for sampling intermediate power values (bugfix for #133)
  - bugfix for stopping prematurely while collecting remaining data
- herd
  - threads now have a configurable timeout for safer runtime (`.run_cmd()`, `.get_file()`, `.put_file()`)
  - cli-command `shell` now has an additional timeout-argument which defaults to 60 minutes
  - add `.min_space_left()` to determine observer fill-level (cli `storage`)
  - add `.service_is_active()`, `.service_is_failed()` to determine status
  - add `.service_get_logs()` & `.service_erase_logs()` to fetch terminal output
  - add separate `.reboot()` to already existing `.poweroff()`
  - add `.kill_sheep_process()` to get a clean slate
  - add `.open()` to re-add hosts that were offline before
  - `.check_status()` now directly monitors sheep-software (not only service)
  - put & copy of files now removes possible prior files at destination
  - progressbar is now more responsive, as it constantly cycles through all still active threads
  - add option to disable progress-bar via `.disable_progress_bar()` and `--no-progress`, to keep logs clean
  - add `.find_invalid_content()` to determine state of files external to DB
- PRU
  - improve over / underflow-protection of variables for harvester, storage, converter
  - allow disabling aux functionality (small overhead not needed for testbed) via `ENABLE_AUX` compile-switch
  - add more unittests for c-code via python-module
  - tests pru-code automatically via GitHub workflow
  - bugfix in statemachine of PRU0 - wait_for_state() sometimes locked up with "reset"
  - simplify debug-switches for PRU1
- kMod
  - fix race-condition bug that prevented start of pru0 (reliably-improvement)
  - disable experimental code - not compatible with non-ti kernel
  - verify canaries less often (~ 2 min)
  - reduce wait-time of kernel-module after pru-firmware is loaded (300 ms -> 10 ms) after analyzing the PRU-init behavior
  - optimize firmware-switching of PRUs (now simultaneous instead of sequential)
  - reboot both PRUs even if only one firmware was changed
  - selecting firmware for Pru0 now also writes accompanying fw for pru1
- py-packaging:
  - allow installing everything via `.[all]`
  - switch to UV (from pip)
  - improve query for version-numbers
- switch to uv for python tooling (on observer)
  - tools are installed via `uv tool install /opt/shepherd/software/python-package/.`
  - for testing there is a jane-venv automatically activated for jane and root (pytest has to be done from `sudo su`)
  - ansible, services and packages are migrated
- datastorage integration -> improve mounting parameters
- switch to uv for dev-environment
  - also for installing py-sheep on observers
  - also for GitHub workflows
- switch to prek as replacement for pre-commit
- ansible
  - remove usage of nelson boot scripts (update kernel & grow partition)
  - try newer non-ti kernel
  - make cleaning-role safer
  - improve kernel preparation
  - switch python components to UV ~~and venv~~
  - improve usage via UV, without venv
  - improve modifications to user-account (custom sudoers-file and generalized .bashrc)
- improve usage of ntpdate for forced resync
- update tooling
- **tested**: pytest sheep, pytest herd windows, pytest shepherd_pru

## 0.9.3

- herd - bugfix for sending Task to sheep
  - always convert to file now
  - ByteIO and StringIO seems broken on some py versions - stream gets corrupted
- sheep - emu / hrv
  - allow custom samplerate for power-tracing - data will be binned by mean() the samples
  - allow to record only power (U * I)
  - **Caution**: resampling IV-Samples with that method might lead to faulty results for target-voltages that are not constant (Sum(U * I) != Sum(U) * Sum(I))

## 0.9.2

- update all links and referenced for moving repos to `nes-lab`
- herd & sheep: transform version into own command
- herd & sheep: allow config be pickled, repickled
  - 10 MB YAML Testbed-tasks takes 350 s to load on sheep
  - that 10 MB has same size as pickle, but loads in .5 s
  - Models get wrapped, dumped to dict and platform-dependant pathlib.Path get replaced by string
- update to gnupru 2025.05
- herd-tool
  - now looks for herd.yaml instead of .yml
  - allow quiet run_task()
  - sort output before it gets printed
- sheep - tracers are now properly disabled (run-conditions were messed up before)
- py-ecosystem - rename logger to log to avoid name-collision
- various small improvements and fixes
- **tested**: pytest sheep, pytest herd windows

## 0.9.1

- adapt to latest naming-changes in core-lib
  - established `ivsurface` and `ivtrace` instead of curves and sample
  - use `Reader.read()` instead of `.read_buffer()`
  - use `Reader.CHUNK_SAMPLES_N`, `Reader.chunks_n`, instead of .buffer_xyz
  - use `UartLogger` instead of #Tracer
- programmer: detect and handle hanging startup by forcing retry
- `GPIOTracer` - implement masking
  - sheep adapts mask to current cape and writes it to PRU
- sheep: emu & hrv mute / avoid some false warnings right after end of experiment
- herd: improve config-finding -> [see doc](https://nes-lab.github.io/shepherd/tools/herd.html#static-config)
- doc: rip out documentation for public instance -> <https://nes-lab.github.io/shepherd-nova/>
- workflows: general improvements
- **tested**: pytest sheep, pytest herd linux & windows, emu with all major vsrc, stress test programmer
- **outdated**: Py VSrc shared lib, most of doc,

## 0.9.0

The main motivation was the replacement of the flawed segmented ring-buffer to a) remove a performance-bottleneck and b) increase reliability.
This unlocked and triggered a lot of other improvements in both regards.

- Buffer replacement
  - old system: 64x 0.1 s segments, bidirectional, 2^14 embedded gpio-events in each segment
  - new: input, output, gpio and utilization has their own buffer
  - input buffer is now also automatically cached in a 64kB OCMC-Section. This allows PRU0 to fetch data itself, but the kernel module must fill it in time (8x 10ms sections) otherwise the PRU has to access the (slow) RAM (reads could be stalled up to 7 us for 8 byte)
  - lots overhead is removed from PRU (more consistent sample-duration), a buffer exchange on the old firmware could cause utilization of >110%
  - kernel module is able to fill OCMC-Cache even with high CPU load! and task overhead is rather small (<5% load)
  - find sweetspots for buffersizes to maximize GPIO-Recording, but don't harm normal operation. RAM-Area is limited to 48 MB, where GPIO now takes 32 MB instead of initially 10
  - added loopback-unittest: fileInp - py - ram - cache - pru - ram - py - fileOut
  - cached buffer is fully verified (correctness via loopback, high load scenario, overhead-estimation on all sub-systems)
- GPIO-Recording
  - gpio-recording is consistent now (race condition in software-mutex), closes #57
  - as GPIO-Sampling-Rate is higher than recording-capability, the system senses back-pressure and drops gpio-samples if buffers are about to overflow
  - worst read-speed was ~ 120 kHz before (1.75 MHz mean, 1.9 MHz max) because PRU1 had to fetch input-buffer for PRU0
  - just READ: min 1.429, mean 2.26, max 2.976 MHz (new sync and util1-stats)
  - always WRITE: min 1.152, mean 1.605, max 1.701 MHz, 112 ns check, 172 ns write
  - pru1 reports 704 ns as worst loop (1.420 MHz), without debug 660 ns (1.515 MHz)
- vPowerSource
  - Emulation from ivsamples uses now 78 % PRU0 (mean), at most 80 % (max)
  - emu with harvesting (from IVSurface) uses 86 % PRU0, at most 89 %  (max)
  - add prototype of battery-model to PRU and also integrate config into shared RAM
  - vharvester - improve similarity to VOC-search by jumping to VOC
- timesync
  - overhaul with big performance improvements, includes an accompanying simulation (in kernel-source) and behaves very similar in reality, fixes #19
  - PI-Algorithm with proper warning via kernel logs (adaptive tuning - 3 stages of accuracy - via error-boundaries)
  - timesync on hardware-level has reached lower boundary as ktime_get_real(), the fastest way to get the time, takes 332 ns
  - PRU uses timer-compensation to slow-down/speed-up (clock-skew with bresenham-algo)
  - improve initial sync for quicker convergence
  - timestamp handling of PRU is supervised by kMod (warn & correct)
  - fix unequal ChipSelect-distance on sync-wrap
- extend Warning-System with the goal to supervise and self-diagnose every critical element during operation
  - timesync: PTP, PHC2SYS and Sys-to-PRU-sync is recorded and faulty states are detected and reported as warning
  - for lab-use NTP is also recorded
  - PRU: utilization of mean and max loop-duration is recorded and broken real-time-condition is reported
  - System-Stats are recorded: CPU-Util, NW-rates, IO-rates, RAM-usage
  - kernel and sheep logs are also recorded
  - PRU errors get reported up the chain and unplanned restarts trigger exceptions
  - if possible the exact timestamps from the reporting services are used
  - buffer-supervisor to detect backpressure, overflows (writer overtakes reader), harmed canaries
  - experiment-supervisor to detect if recorder missed start or ended too early
  - canaries (4 in buffers, 12 in shared memory)
- PRU
  - more direct memory access (before it had 2 layers of pointer-translation)
  - overhaul of state-machines, remove mutexes
  - clean up build system
  - unify message-system
  - cores record their own util-stats
- KernelModule
  - more correct and modern usage of kernel-API
  - cleaner start/stop of submodules
  - periodically check canaries
  - access and fill-routines for OCMC-cache (fast intermediate buffer)
  - bind io-mem without cache
- PythonSheep
  - more modular code (most files now < 500 LOC)
  - new data-flow: source dictates the chunk-size, the sink deals with it (or complains early)
  - progress-bar during filling initial buffer and during experiment
  - buffers get monitored to detect back-pressure (and react to it)
  - detector for buffer overflows and possible blind spots during detection (low polling rate)
  - optimize write operation for GPIO - resulting in 3x more throughput - from 9M Events to ~ 26M in 60 s
  - Benchmark writing full gpio-load, with lots of discarded buffer-segments
    - full-lzf, 60s, 13.3M GPIO, 105 MB
    - gpio-None, 60s, 22.6M GPIO, 257 MB
    - full-None, 60s, 26.0M+ GPIO, 356 MB, all on external uSD (36M discarded)
  - repaired unittests
  - make set_stop() & set_start() safer, less prone to raise
- GitHub-Actions
  - also test herd on windows & macOS
  - extend tests to python 3.13
  - release via tagging
  - more modular, sub-jobs getting triggered by action
  - prepare release to pypi via trusted publishing

## 0.8.5

- sheep bugfix that prevented clean exit after execution (unhandled filled queue did not release thread)
- hw-designfiles - add cape 2.5e & move prior capes to `_deprecated`

## 0.8.4

- sheep programming needed some improvements
  - bugfix - don't realign nrf-hex-file with 16bit address limit
  - workaround - reduce default data-rate for programming (500k to 200k)
  - bugfix - properly report programming errors (write-error, verify, parsing was not reported correctly)
  - ihex - added remaining 3 of 6 command-types of intel hex
  - ihex - corrected calculation of Extended Segment Address
  - ihex - more detailed error-reporting in python (including line-number)
  - ihex - full 32bit address-space should now be usable (was limited to <64k before)
  - ihex - detection of malformed command records
  - ihex - detection of unknown commands (throw error)
  - error-reporting did not detect a pru-restart
  - programmer now retries 5 times before failing
    - also the data-rate gets reduced by ~~20~~ 40 % after each failed attempt
- sheep
  - now logs usage (timestamp, sub-command i.e. `run`, total runtime)
  - `shepherd-sheep eeprom read -f` prints full data-model
  - `shepherd-sheep eeprom read -r` prints only hardware revision of cape
  - small optimizations (fail early, but avoid exception; avoid code duplication)
- herd
  - fix bug on Windows OS while distributing files
  - use PurePosixPath for all remote paths (better cross-compatibility)
  - some run_cmd() executions have been silenced (from info to debug-level)
  - `shepherd-herd retrieve` now alternatively takes local task/job-file and fetches embedded paths
  - `shepherd-herd retrieve` does not add hostname to filename if already present
  - `shepherd-herd alive` had a bug and reported the opposite
  - `shepherd-herd status` now also reports last testbed-usage as timestamp and timedelta
- python
  - avoid os-package if pathlib can handle it
  - avoid sys.exit() if click.context.exit() is available
- hw-designfiles - add cape 2.5d & move prior capes to `_deprecated`
- ansible - avoid updating kernel
- **tested**: pytest sheep, pytest herd linux & windows

## 0.8.3

- setup
  - fix ambitious removal of ciphers for secure host
  - test and adapt to raspberry pi OS
  - create smaller playbook to redeploy roles (`dev_redeploy_roles.yml`)
- herd
  - fix StringIO-Bug
- timesync: improve configuration for client and server
- sync analysis: move to `software/debug_analyze_time_sync` and also add CLI
- vsrc comparison: move to `software/debug_compare_vsrouces`
- py
  - fix > 100 linting error
  - improve exception-system
  - make compatible with latest core-lib 2024.11.3
- pru
  - extend error-system
  - refactor and fix messaging-system
- **tested**: pytest sheep, pytest herd, playbook dev_rebuild_sw.yml

## 0.8.2

- PRU now gets partially zeroed buffer-segments
- PRU had a race-condition with a loose mutex resulting in keeping old gpio-samples
- python warns on full gpio-buffer (as it can only hold ~16k entries in 100 ms)
- python warns if first or last timestamp of gpio-buffer is out of scope of outer buffer-period
- hw cape - add errata-list
- vsrc - add datatype to determine state-variables
- CalibrationPair - add units
- split pru0-shepherd-fw into hrv & emu -> kModule, shepherd-sheep, playbooks, workflows adapted
- pru-vsource - add feedback to harvester
- pru-harvester - add feedback & extrapolation for cv-harvester
- **tested**: pytest sheep, pytest herd, playbook dev_rebuild_sw.yml
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

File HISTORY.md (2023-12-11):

# History of Changes

## 0.7.2

- linux
  - switch to real-time kernel
  - make phc2sys & ptp4l more reliable
- kernel-module
  - cleanup, optimize
  - more futureproof
- python
  - reduce load by 50 % (omit timestamps & change compression)
- toolchain
  - replace isort, black, flake8 by ruff
- debug
  - add option to generate kernel gpio edges (`trigger_loop_callback()` in `pru_sync_control.c`)
  - allow analyzing recorded gpio sync traces (`software/test_timesync`)
- update floorplan of testbed

## 0.7.1

- python
  - speed improvements, linting, simplifications
  - optimize for py310..py312
  - safer sheep-shutdown
  - fully type-hinted
  - more error-catching
  - more responsive monitor-threads
  - identify and try to avoid deadlocks and infinite loops
- improve timesync reliability (phc2sys & ptp4l)
- forbid unsafe ssh cypher
- update deps

## 0.7.0

- pru-firmware:
   - improve blind-spots of gpio-sampling
   - fix compiler warning (cgt & gcc)
   - [measure timings](https://github.com/orgua/shepherd_v2_planning/blob/main/scratch/pruBenchmark_2023_10.md)
   - bugfixes
- sheep
   - refactoring of monitors
   - repair ptp & dmesg / kernel logging
   - repair uart-monitor
   - allow to record stdout of sheep
   - set gpio-direction to input for now
   - redo logging-system
- herd
   - more reliable (needs to enter context now)
   - tests availability of nodes / sheep
   - redo logging-system
   - refactor
   - improve doc
   - more functionality in herd-class
- doc
   - improve details
   - add info about testbed and subprojects
- ansible
   - tweaks, speedups
   - fixes
   - (timesync) services are now more reliable
   - update kernel version
   - lots of linting
   - script to activate emmc-flasher
- cal
   - lots of tweaks and fixes
- **tested**: ansible-installer, herd, sheep

## v0.4.5 - 2023.08.23

- add option to build an inventory
- herd, sheep, cal-tool: fully integrate datalib
- sheep
  - improve exit behavior
  - various small improvements, refactorings
  - speed-improvements through tracing
- ansible:
  - safer pipes
  - bugfixes
- pru-programmer: bugfixes, add direction pin, test with new target
- integrate other shepherd-projects as submodules
- ubuntu 22.04 now default distribution for sheep (py 3.10)
- cal-tool uses typer for cli now
- **tested**: shepherd-sheep & -herd

## 0.4.4 - 2023.02.26

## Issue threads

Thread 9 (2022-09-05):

### ISSUE TITLE
add support for WSL2

### ISSUE THREAD

**Issue by fedy0** [nes-lab/shepherd#9]
I prepared and tested a script to setup the latest WSL (WSL2) and [usbipd](https://github.com/dorssel/usbipd-win) services but I want to know if its needed for easy-of-test of the gcc-port on Windows.

IMHO, I think it would be helpful and better than a traditional virtual machine as WSL2 comes with kernels and one can easily swap between its version and that of the kernels.

I currently don't know how the firmware is deployed (not yet familiar with ansible) but I added usbipd just incase if we need usb sharing services between Windows and WSL2, all in a single click.

Lastly, if I am to add the script and its README, what location is preferred? `./software/gcc-port` and `./docs`  or both in `./software/gcc-port` or add none?

**Comment by orgua** [comment]
Well first, the usual starting-point is having a running linux at hand. There are sufficient resources online for installing WSL if you want to use windows. It is not supported by us, as stated [here](https://github.com/orgua/shepherd/blob/master/docs/user/getting_started.rst). Additionally WSL-Routines still keep changing, last time with WSL2.

Second, what would a user need usbipd for? The only thing I can think of is your special use-case. Or did i miss something? I didn't try this yet, but is usb-sharing really needed? I thought there will be a com-port for ssh. 
Did you manage to fully setup a beaglebone connected via USB? How about providing Internet-Access and running ptp / ntp? It looks like this is too niche to include in the repo. The usual and preferred way is to include the BBs into your LAN. 

thirdly: yes, WSL is far more helpful and usable than a VM :)

at last but not least: usage of shell-scripts is somehow outdated - there are more secure and better documented alternatives available. Shepherd uses ansible. The few steps for bootstrapping the process (beforehand) are documented in readme-files. 

So no, integration of the script into the repo is unlikely, but you are welcome to post your script here in this issue - so others can find it. 

Just for completion: WSL is not needed in windows. you can ssh from a normal shell, same goes for python / ansible. And linux-bound cross-compilation could be run on the BB itself.

**Comment by fedy0** [comment]
Ok,
I just added the WSL2 and usbipd script [here](https://gist.github.com/fedy0/09f7edd64a5176ad834f095f27e27864)

I hope it helps someone.

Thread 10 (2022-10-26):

### ISSUE TITLE
use crosstool-ng & regenerate 

### ISSUE THREAD

**Issue by fedy0** [nes-lab/shepherd#10]
@orgua I have been thinking about regenerating the toolchain we've been using to see if some of the errors ([here](https://github.com/orgua/shepherd/blob/gcc-port/software/gcc-port/firmware/README.md)  and [there](https://github.com/orgua/shepherd/blob/gcc-port/software/gcc-port/firmware/readme_overflow_issue.md)) that seem internal to the compiler will reduce.
I've little experience with crosstool-ng.
Do I try it?
I'm asking before hand because it takes a while to generate the toolchain.
What do you think?

**Comment by orgua** [comment]
Just for reference: you are talking about the c-code for the PRUs on the beaglebone.

We are currently using two different cross-compilers (TI's CGT and GCC with PRU-Extension) for the PRU-Code. One compiler (cgt) has trouble calculating correct results with u64, the other currently produces non-optimal code and therefore overflows the program memory. Additionally we use a basic makefile, comparable to a bash-script, to feed the compiler. That's our current "chain of tools".

If you know a way to get rid of these constraints go for it. It should be a good exercise to learn more about embedded software development.

**Comment by orgua** [comment]
ok, closing this. CGT works for now and GCC saw big improvements [lateley ](https://github.com/dinuxbg/gnupru/issues/43#issuecomment-1272528295)

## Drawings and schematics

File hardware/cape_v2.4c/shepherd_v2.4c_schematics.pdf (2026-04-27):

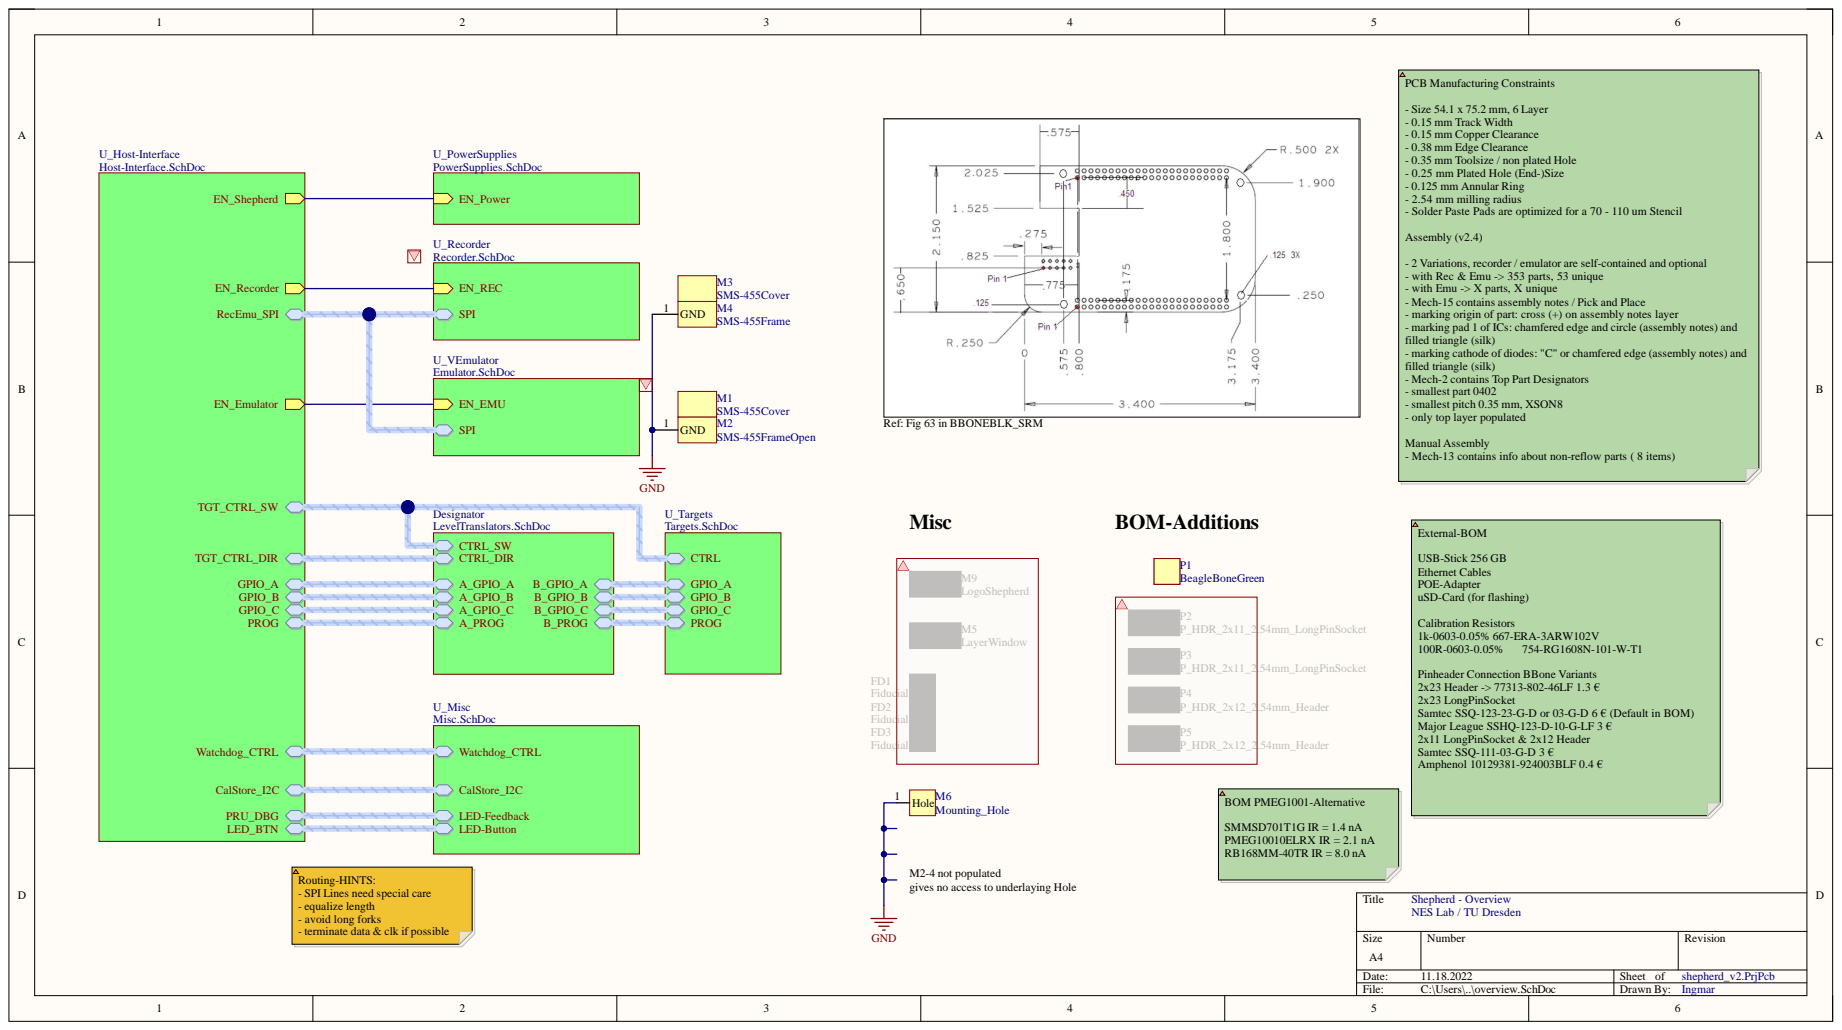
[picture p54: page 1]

- Size 54.1 x 75.2 mm, 6 Layer
- 0.15 mm Track Width
- 0.15 mm Copper Clearance
- 0.38 mm Edge Clearance
- 0.35 mm Toolsize / non plated Hole
- 0.25 mm Plated Hole (End-)Size
- 0.125 mm Annular Ring
- 2.54 mm milling radius
- Solder Paste Pads are optimized for a 70 - 110 um Stencil

- 2 Variations, recorder / emulator are self-contained and optional
- with Rec & Emu -> 353 parts, 53 unique
- with Emu -> X parts, X unique
- Mech-15 contains assembly notes / Pick and Place
- marking origin of part: cross (+) on assembly notes layer
- marking pad 1 of ICs: chamfered edge and circle (assembly notes) and
filled triangle (silk)
- marking cathode of diodes: "C" or chamfered edge (assembly notes) and
- Mech-2 contains Top Part Designators
- smallest part 0402
- smallest pitch 0.35 mm, XSON8
- only top layer populated

Manual Assembly
- Mech-13 contains info about non-reflow parts ( 8 items)

USB-Stick 256 GB
Ethernet Cables
POE-Adapter
uSD-Card (for flashing)

Pinheader Connection BBone Variants
2x23 Header -> 77313-802-46LF 1.3 €
2x23 LongPinSocket
Samtec SSQ-123-23-G-D or 03-G-D 6 € (Default in BOM)
Major League SSHQ-123-D-10-G-LF 3 €
2x11 LongPinSocket & 2x12 Header
Samtec SSQ-111-03-G-D 3 €
Amphenol 10129381-924003BLF 0.4 €

M2-4 not populated
gives no access to underlaying Hole

Routing-HINTS:
- SPI Lines need special care
- equalize length
- avoid long forks
- terminate data & clk if possible

Shepherd - Overview
NES Lab / TU Dresden

Size A4 | Number | Revision

Date: 11.18.2022 | Sheet of shepherd_v2.PrjPcb
File: C:\Users\..\overview.SchDoc | Drawn By: Ingmar

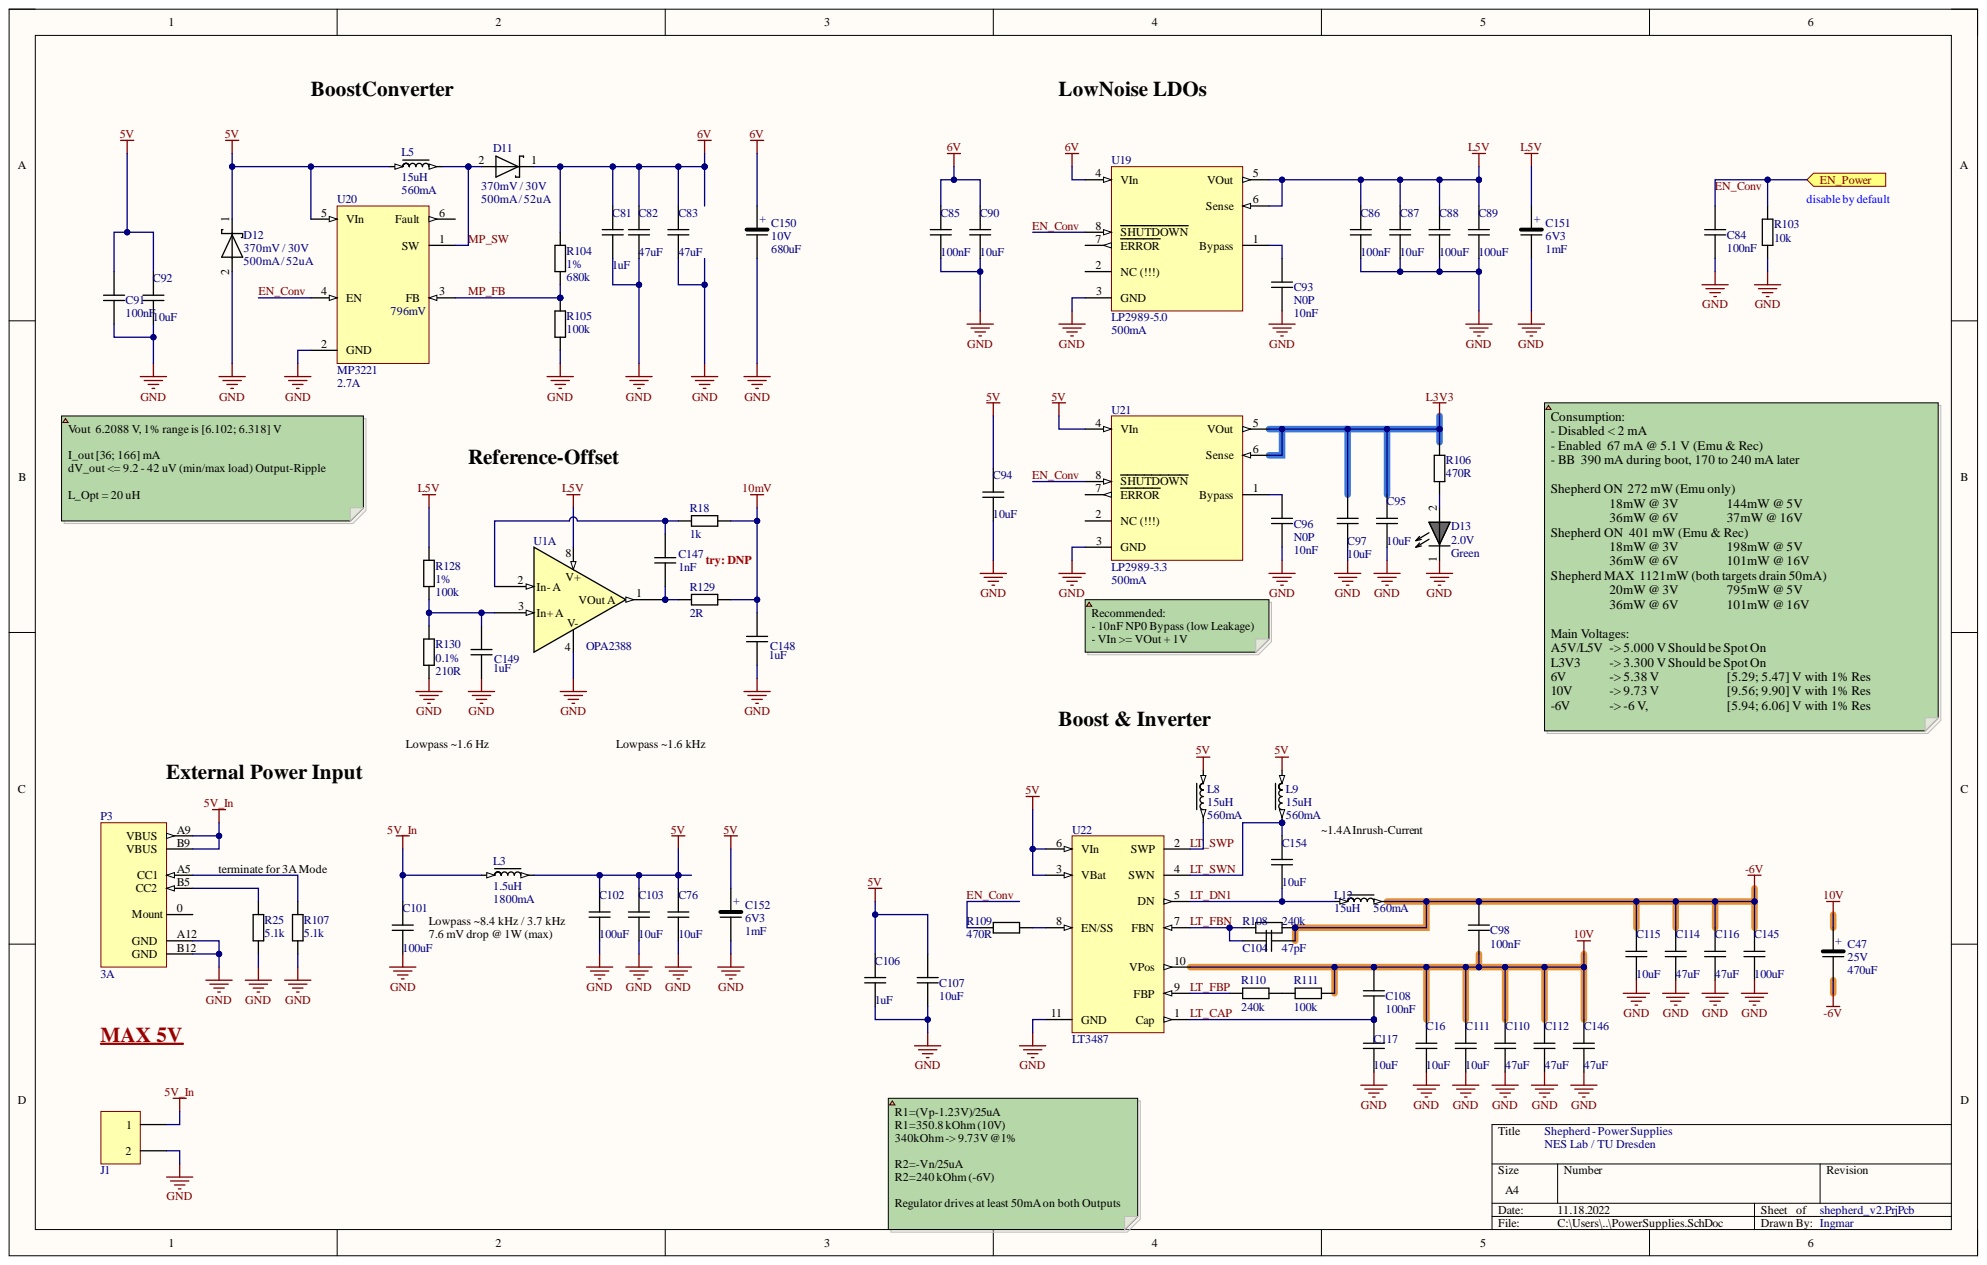
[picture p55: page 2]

Consumption:
- Disabled < 2 mA
- Enabled 67 mA @ 5.1 V (Emu & Rec)
- BB 390 mA during boot, 170 to 240 mA later

I_out [36; 166] mA
dV_out <= 9.2 - 42 uV (min/max load) Output-Ripple

Shepherd ON 272 mW (Emu only)

Shepherd ON 401 mW (Emu & Rec)

Shepherd MAX 1121mW (both targets drain 50mA)

Main Voltages:
A5V/L5V -> 5.000 V Should be Spot On

Shepherd - Power Supplies
NES Lab / TU Dresden

Regulator drives at least 50mAon both Outputs

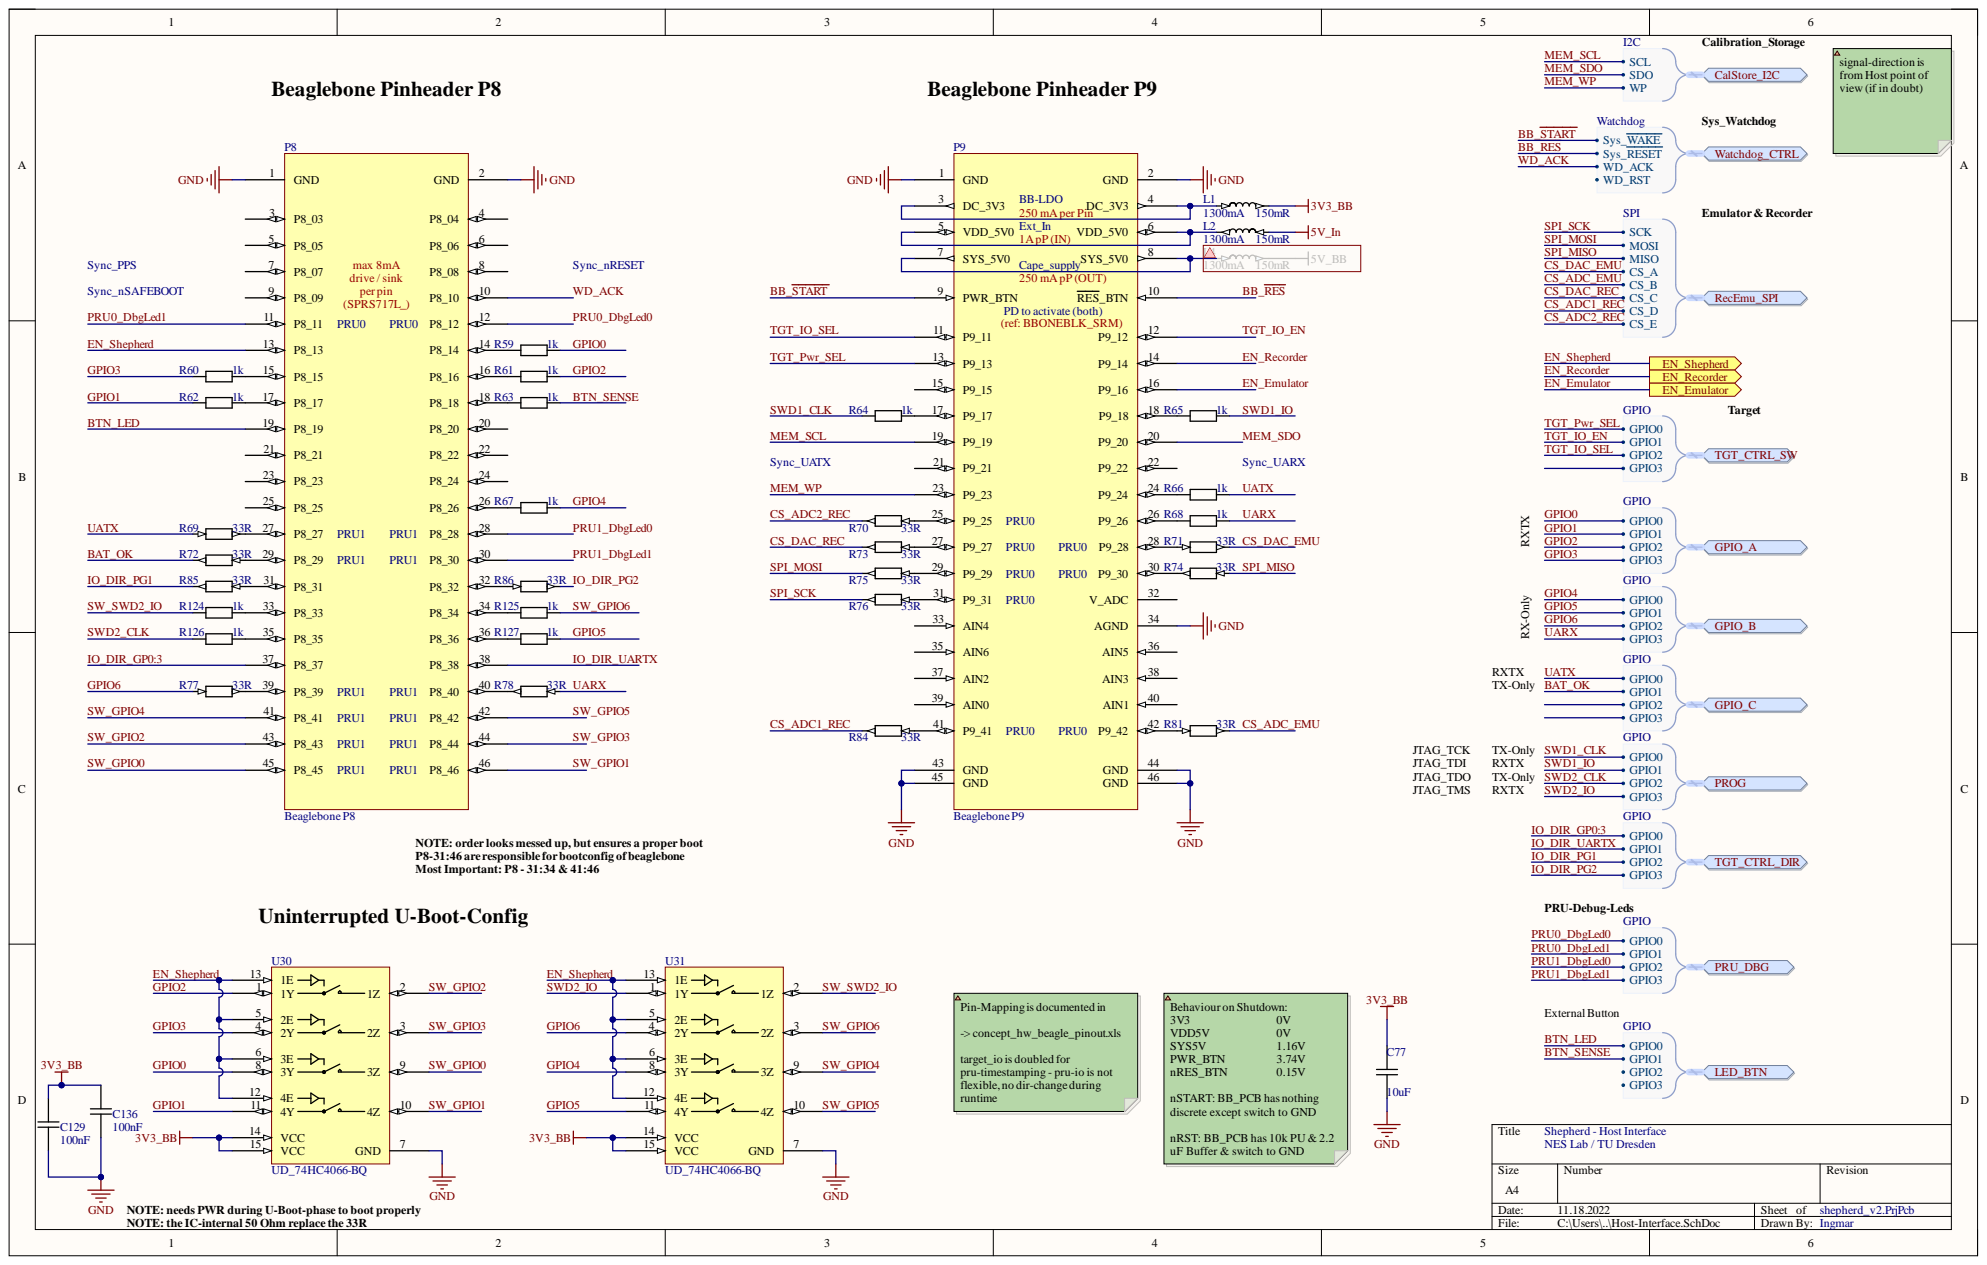
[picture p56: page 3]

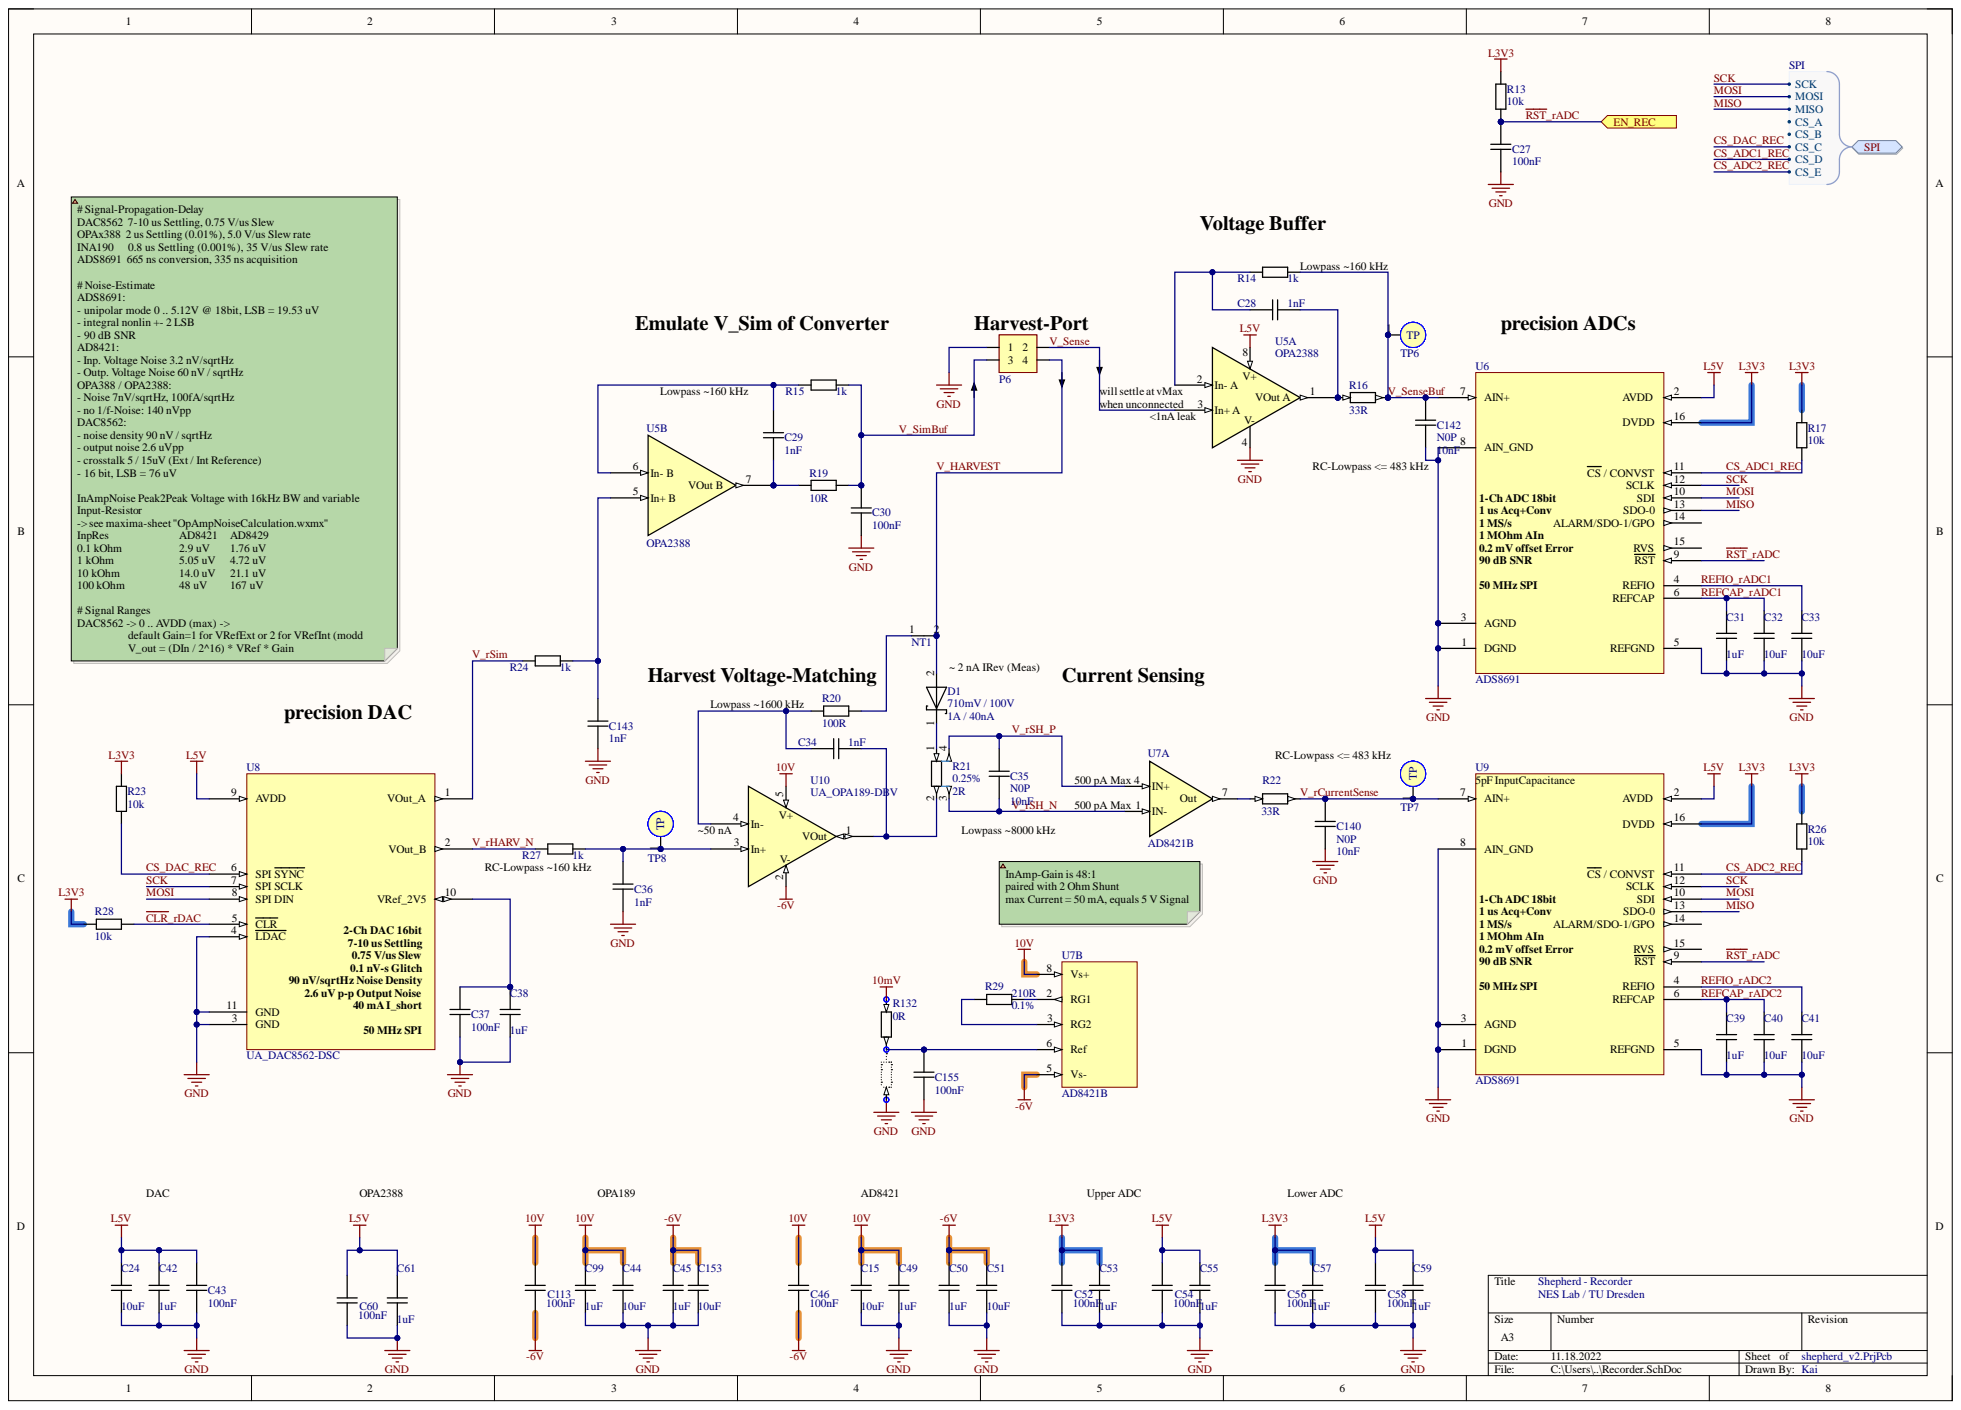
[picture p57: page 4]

# Signal-Propagation-Delay
DAC8562 7-10 us Settling, 0.75 V/us Slew
OPAx388 2 us Settling (0.01%), 5.0 V/us Slew rate
ADS8691 665 ns conversion, 335 ns acquisition

# Noise-Estimate
ADS8691:
- unipolar mode 0 .. 5.12V @ 18bit, LSB = 19.53 uV
- integral nonlin +- 2 LSB
- 90 dB SNR
- Inp. Voltage Noise 3.2 nV/sqrtHz
- Outp. Voltage Noise 60 nV / sqrtHz
OPA388 / OPA2388:
- Noise 7nV/sqrtHz, 100fA/sqrtHz
- no 1/f-Noise: 140 nVpp
DAC8562:

- noise density 90 nV / sqrtHz
- output noise 2.6 uVpp
- crosstalk 5 / 15uV (Ext / Int Reference)
- 16 bit, LSB = 76 uV

InAmpNoise Peak2Peak Voltage with 16kHz BW and variable
Input-Resistor
->see maxima-sheet "OpAmpNoiseCalculation.wxmx"

default Gain=1 for VRefExt or 2 for VRefInt (modd
V_out = (DIn / 2^16) * VRef * Gain

InAmp-Gain is 48:1
paired with 2 Ohm Shunt
max Current = 50 mA, equals 5 V Signal

90 nV/sqrtHz Noise Density
2.6 uV p-p Output Noise

Shepherd - Recorder
NES Lab / TU Dresden

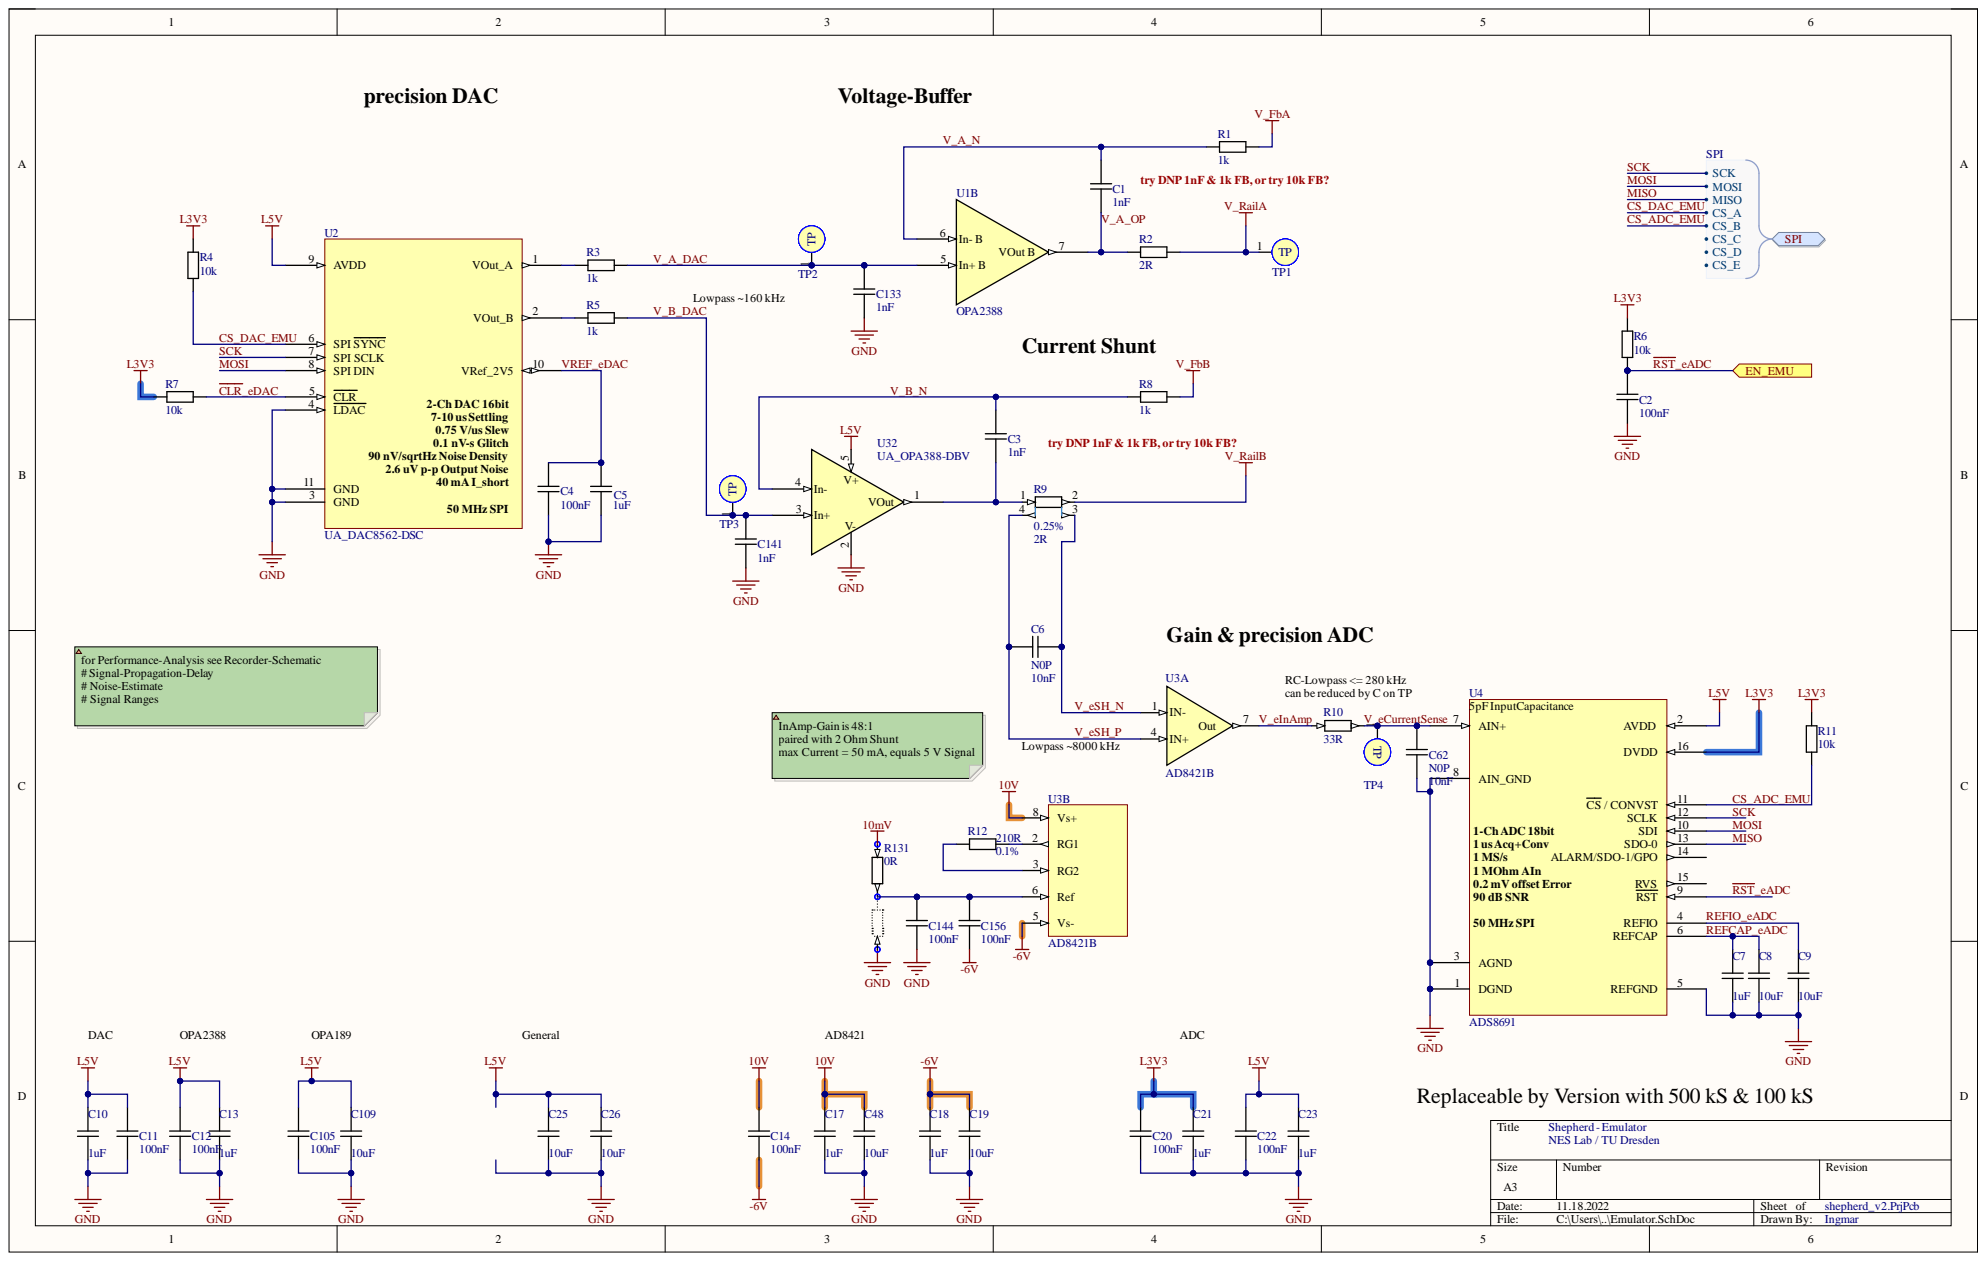
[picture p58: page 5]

try DNP 1nF & 1k FB, or try 10k FB?

90 nV/sqrtHz Noise Density
2.6 uV p-p Output Noise

for Performance-Analysis see Recorder-Schematic
# Signal-Propagation-Delay
# Noise-Estimate
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

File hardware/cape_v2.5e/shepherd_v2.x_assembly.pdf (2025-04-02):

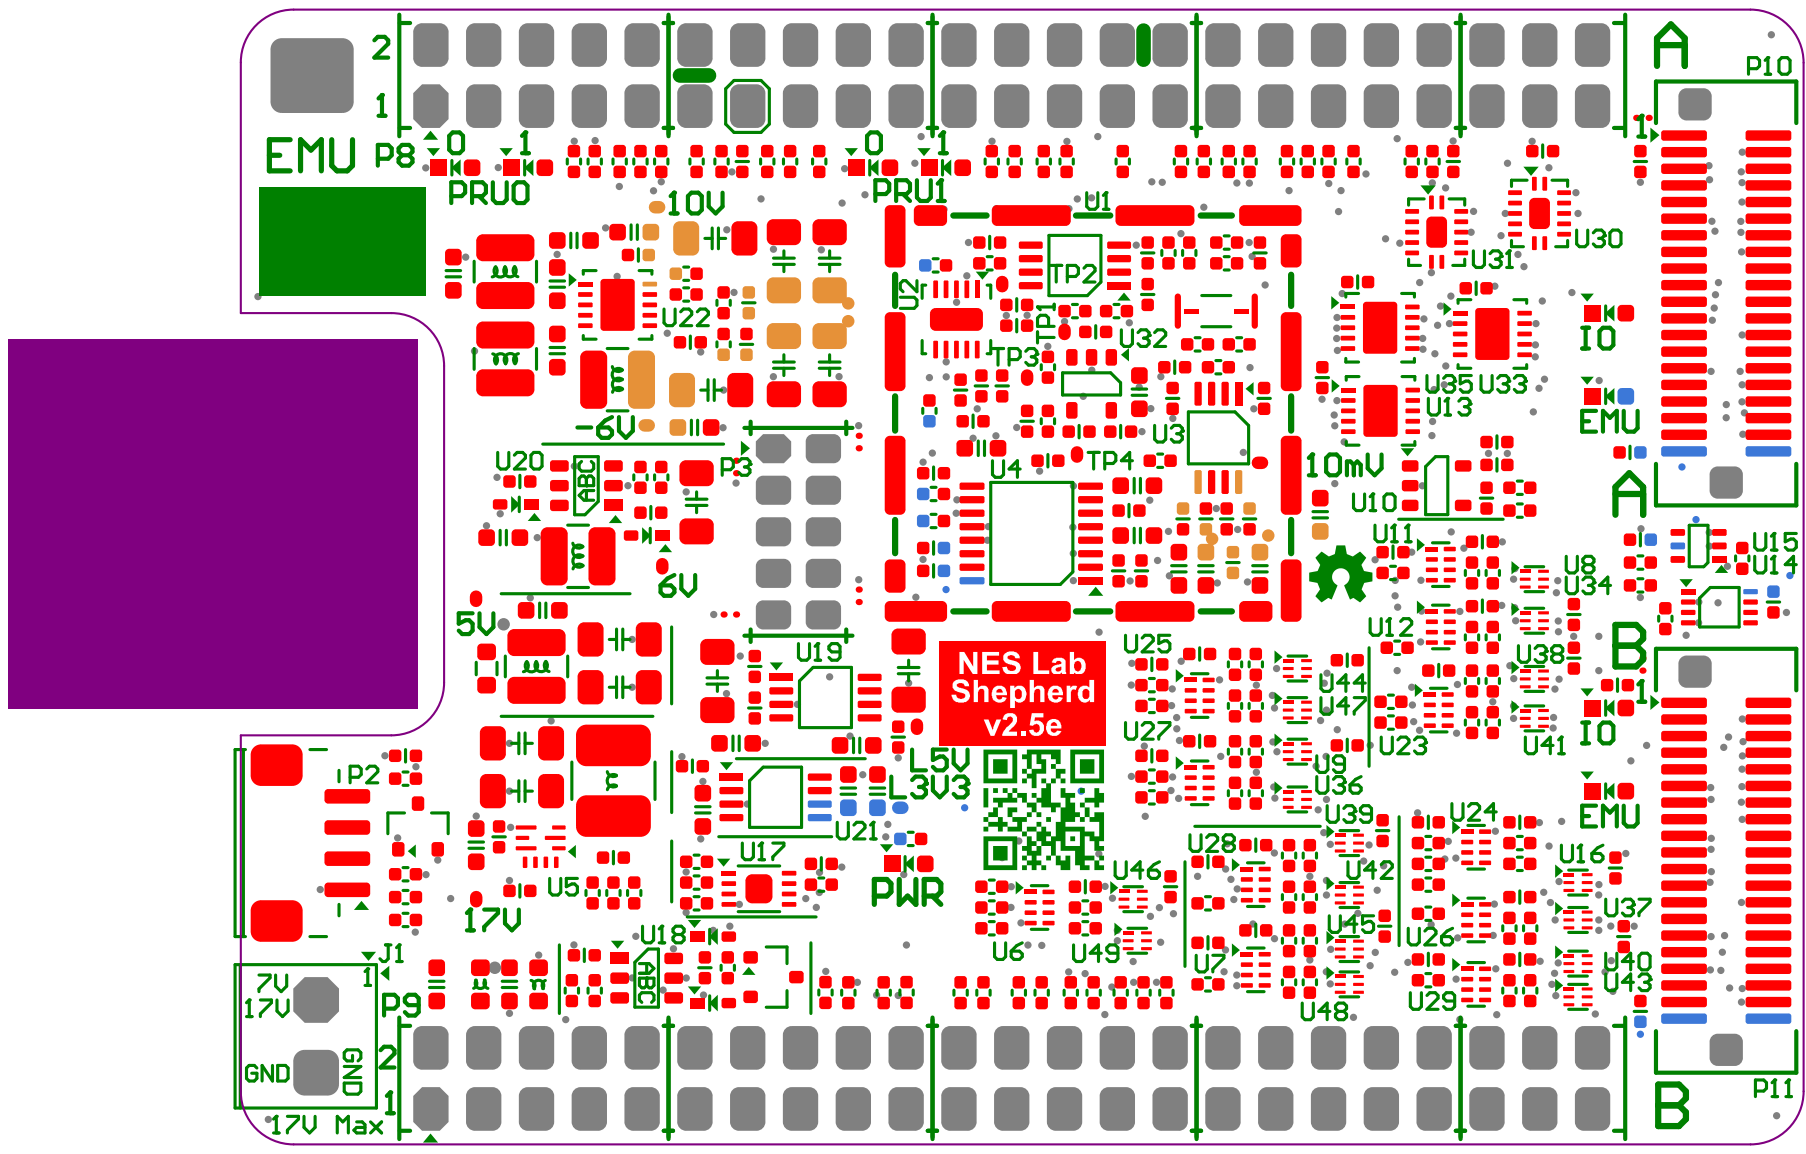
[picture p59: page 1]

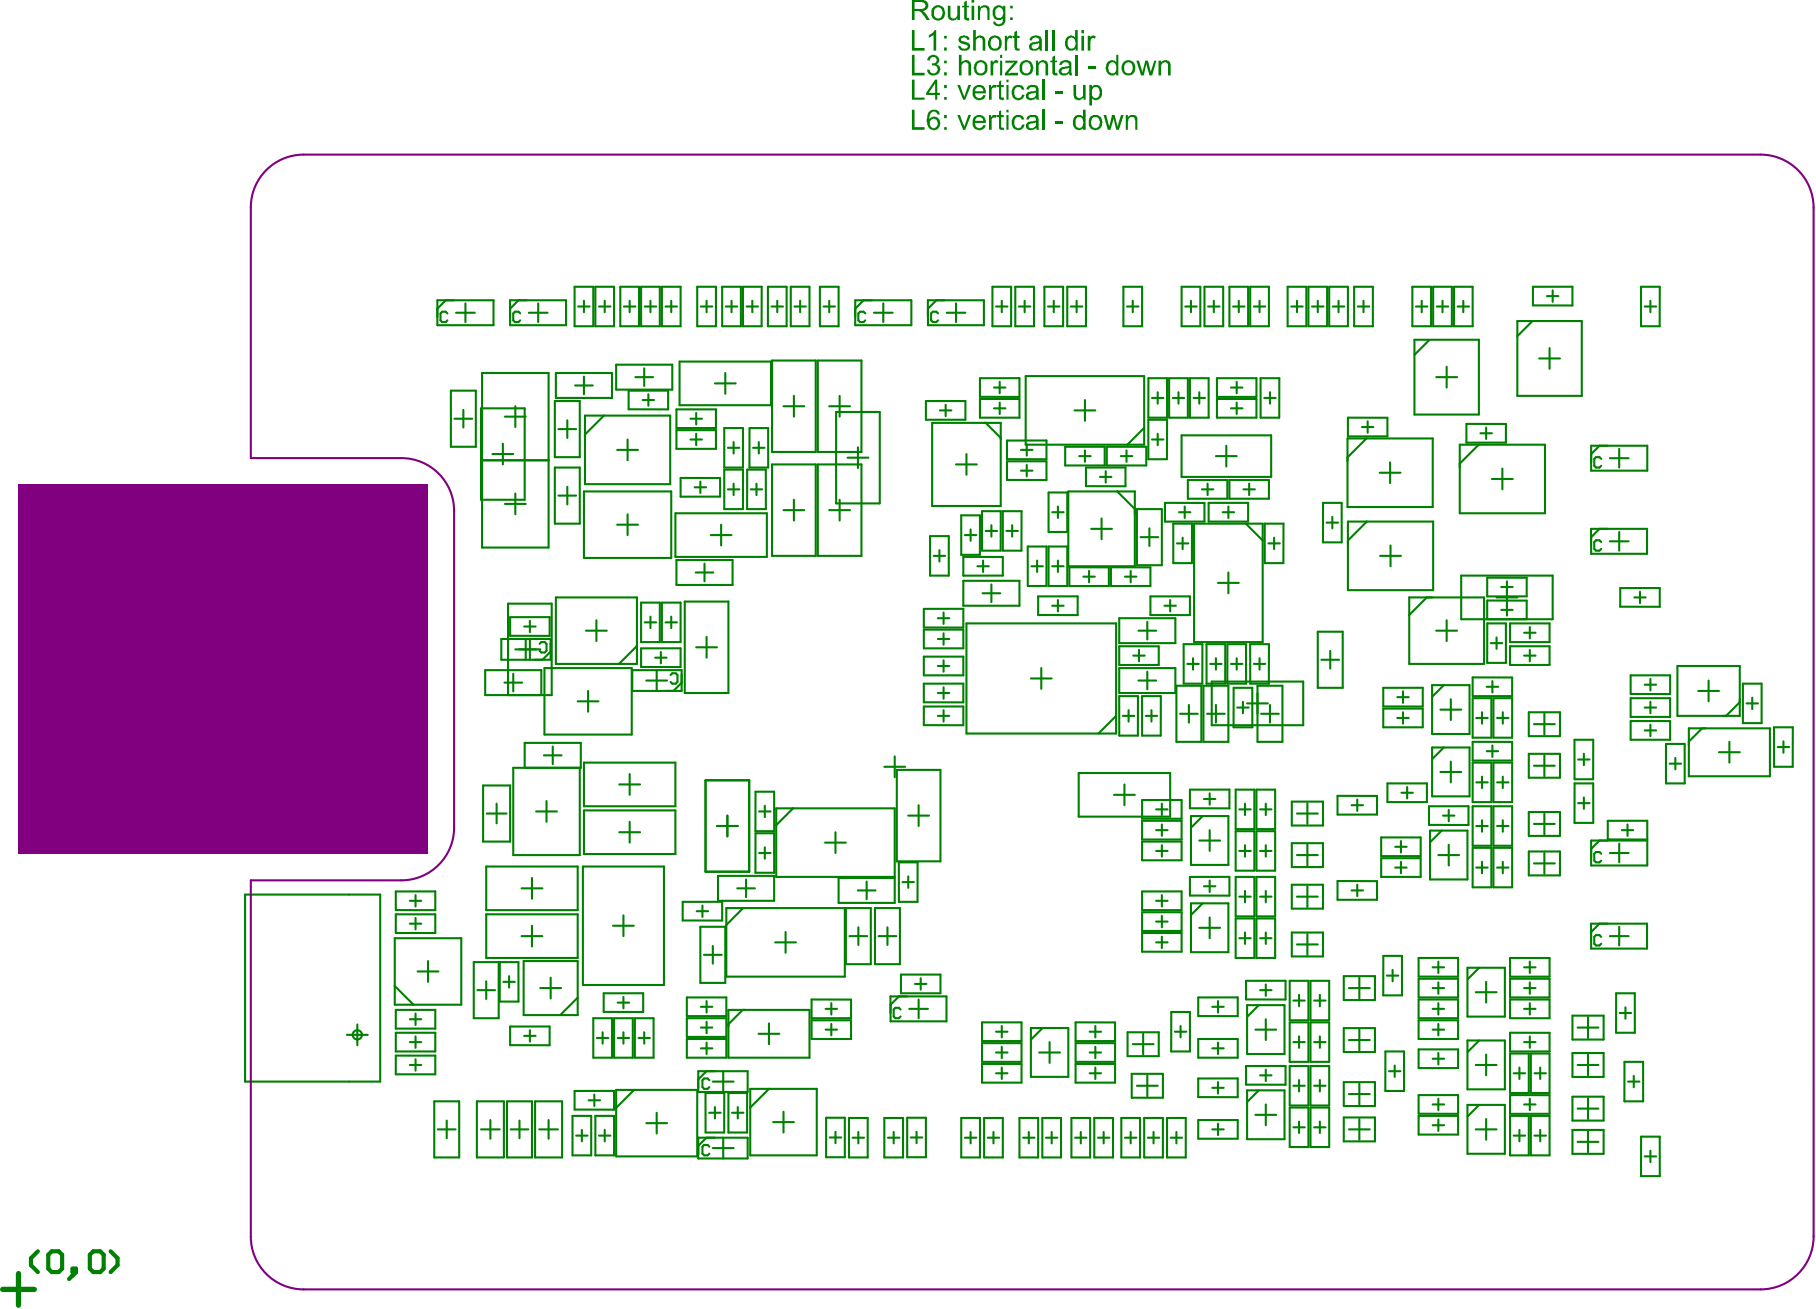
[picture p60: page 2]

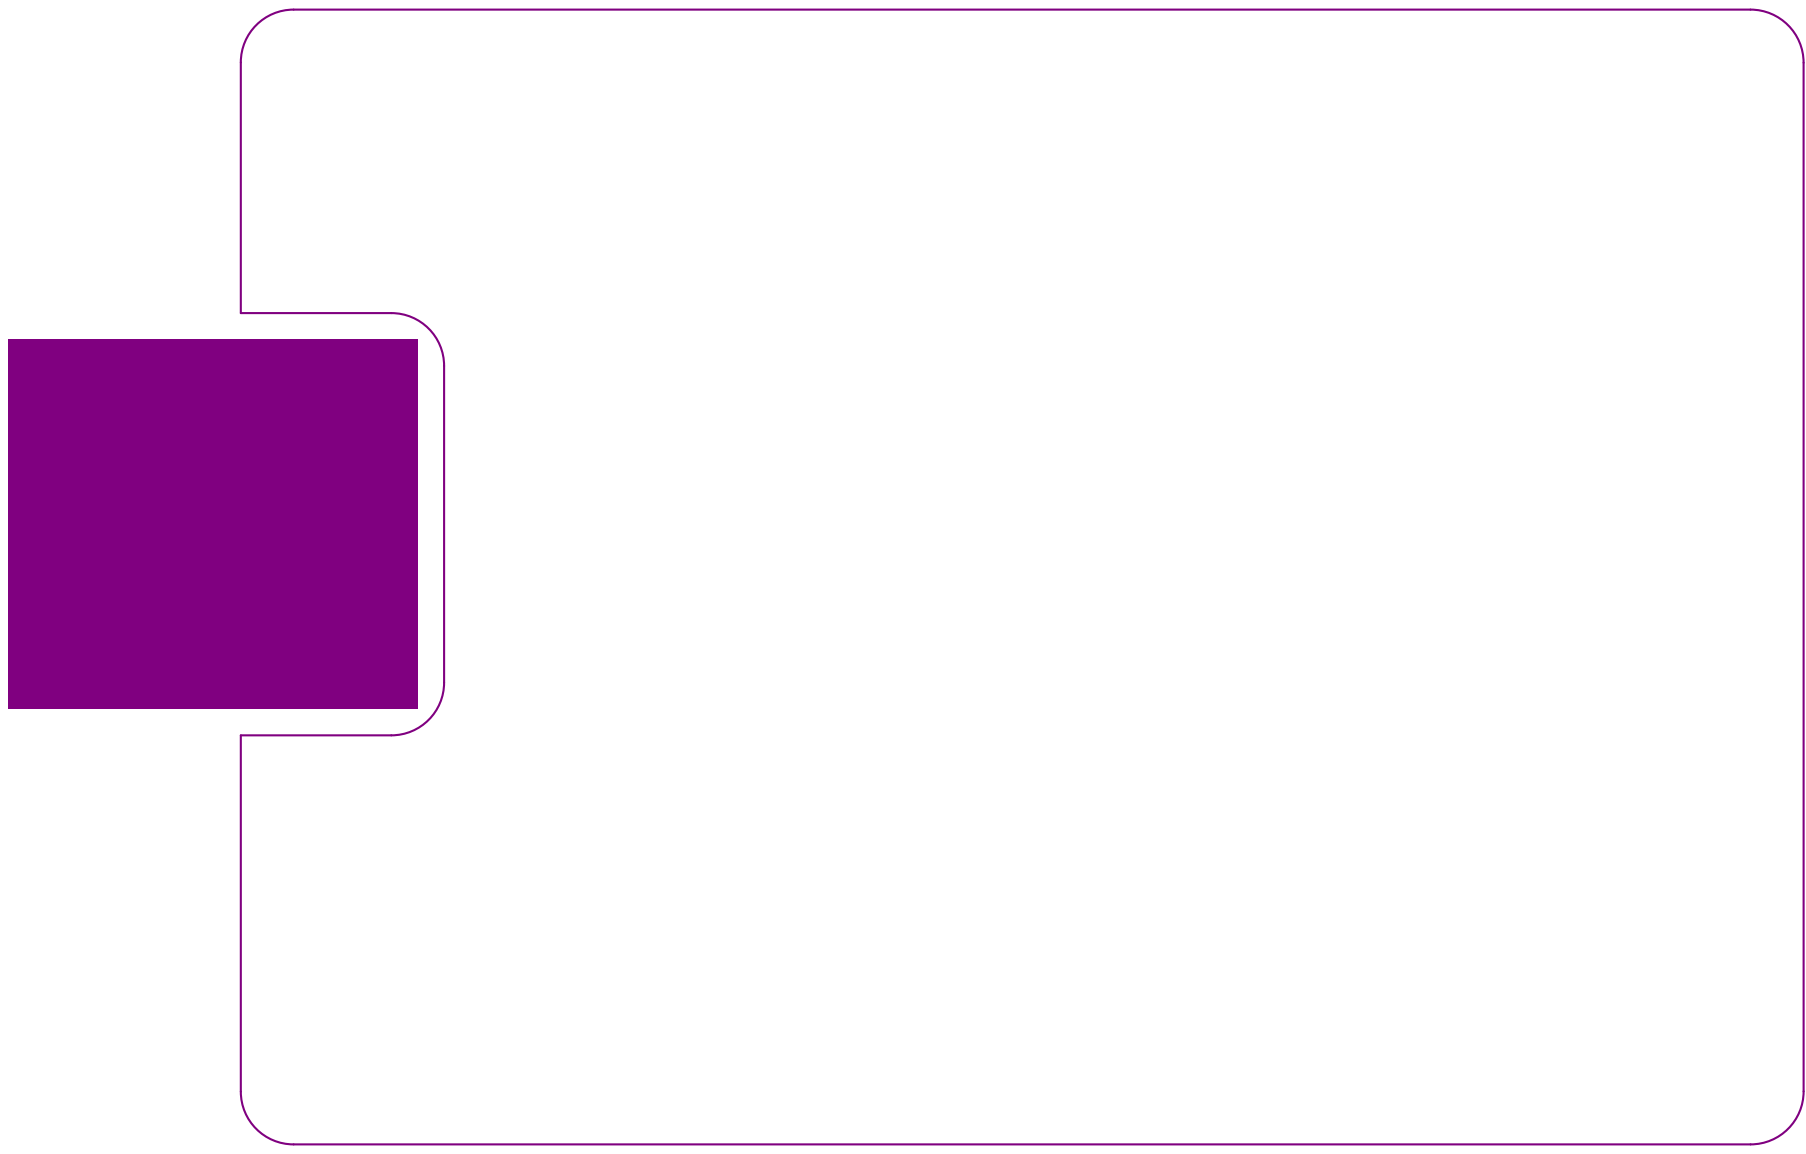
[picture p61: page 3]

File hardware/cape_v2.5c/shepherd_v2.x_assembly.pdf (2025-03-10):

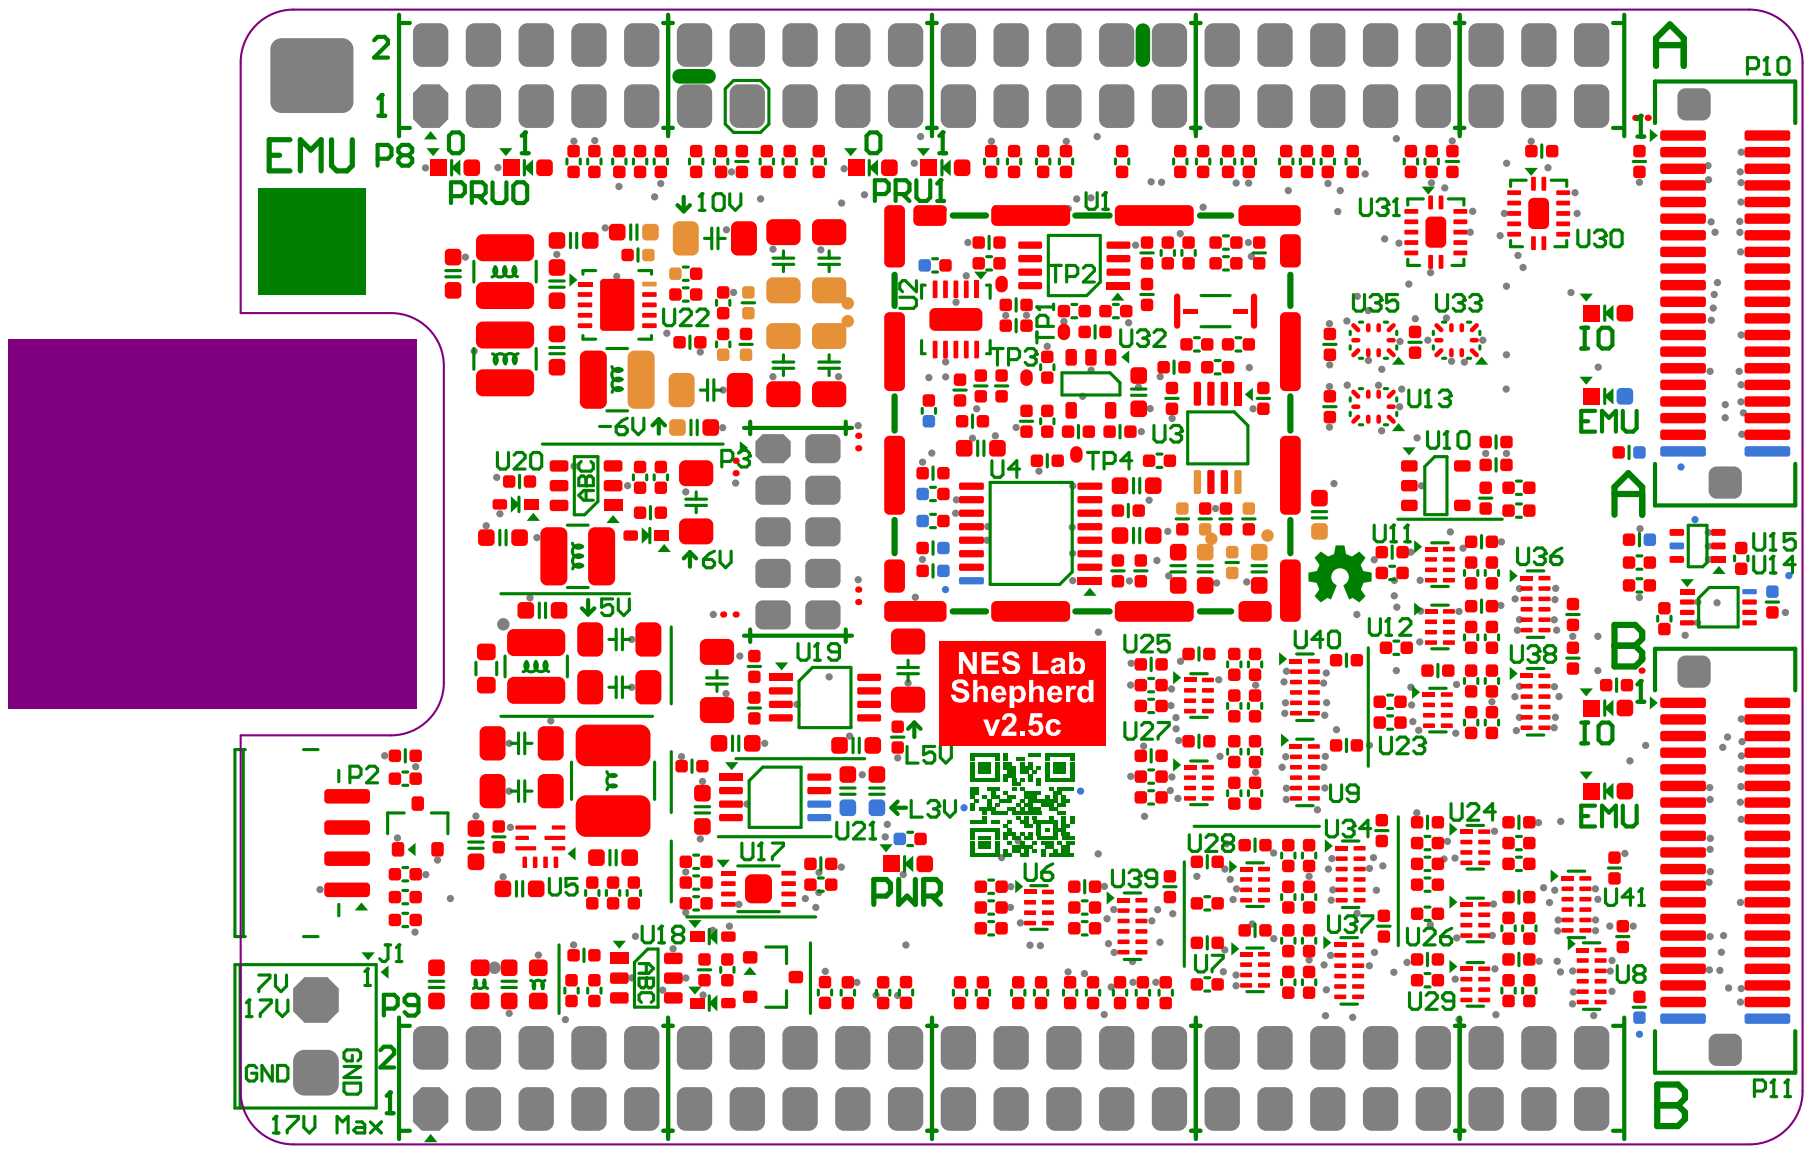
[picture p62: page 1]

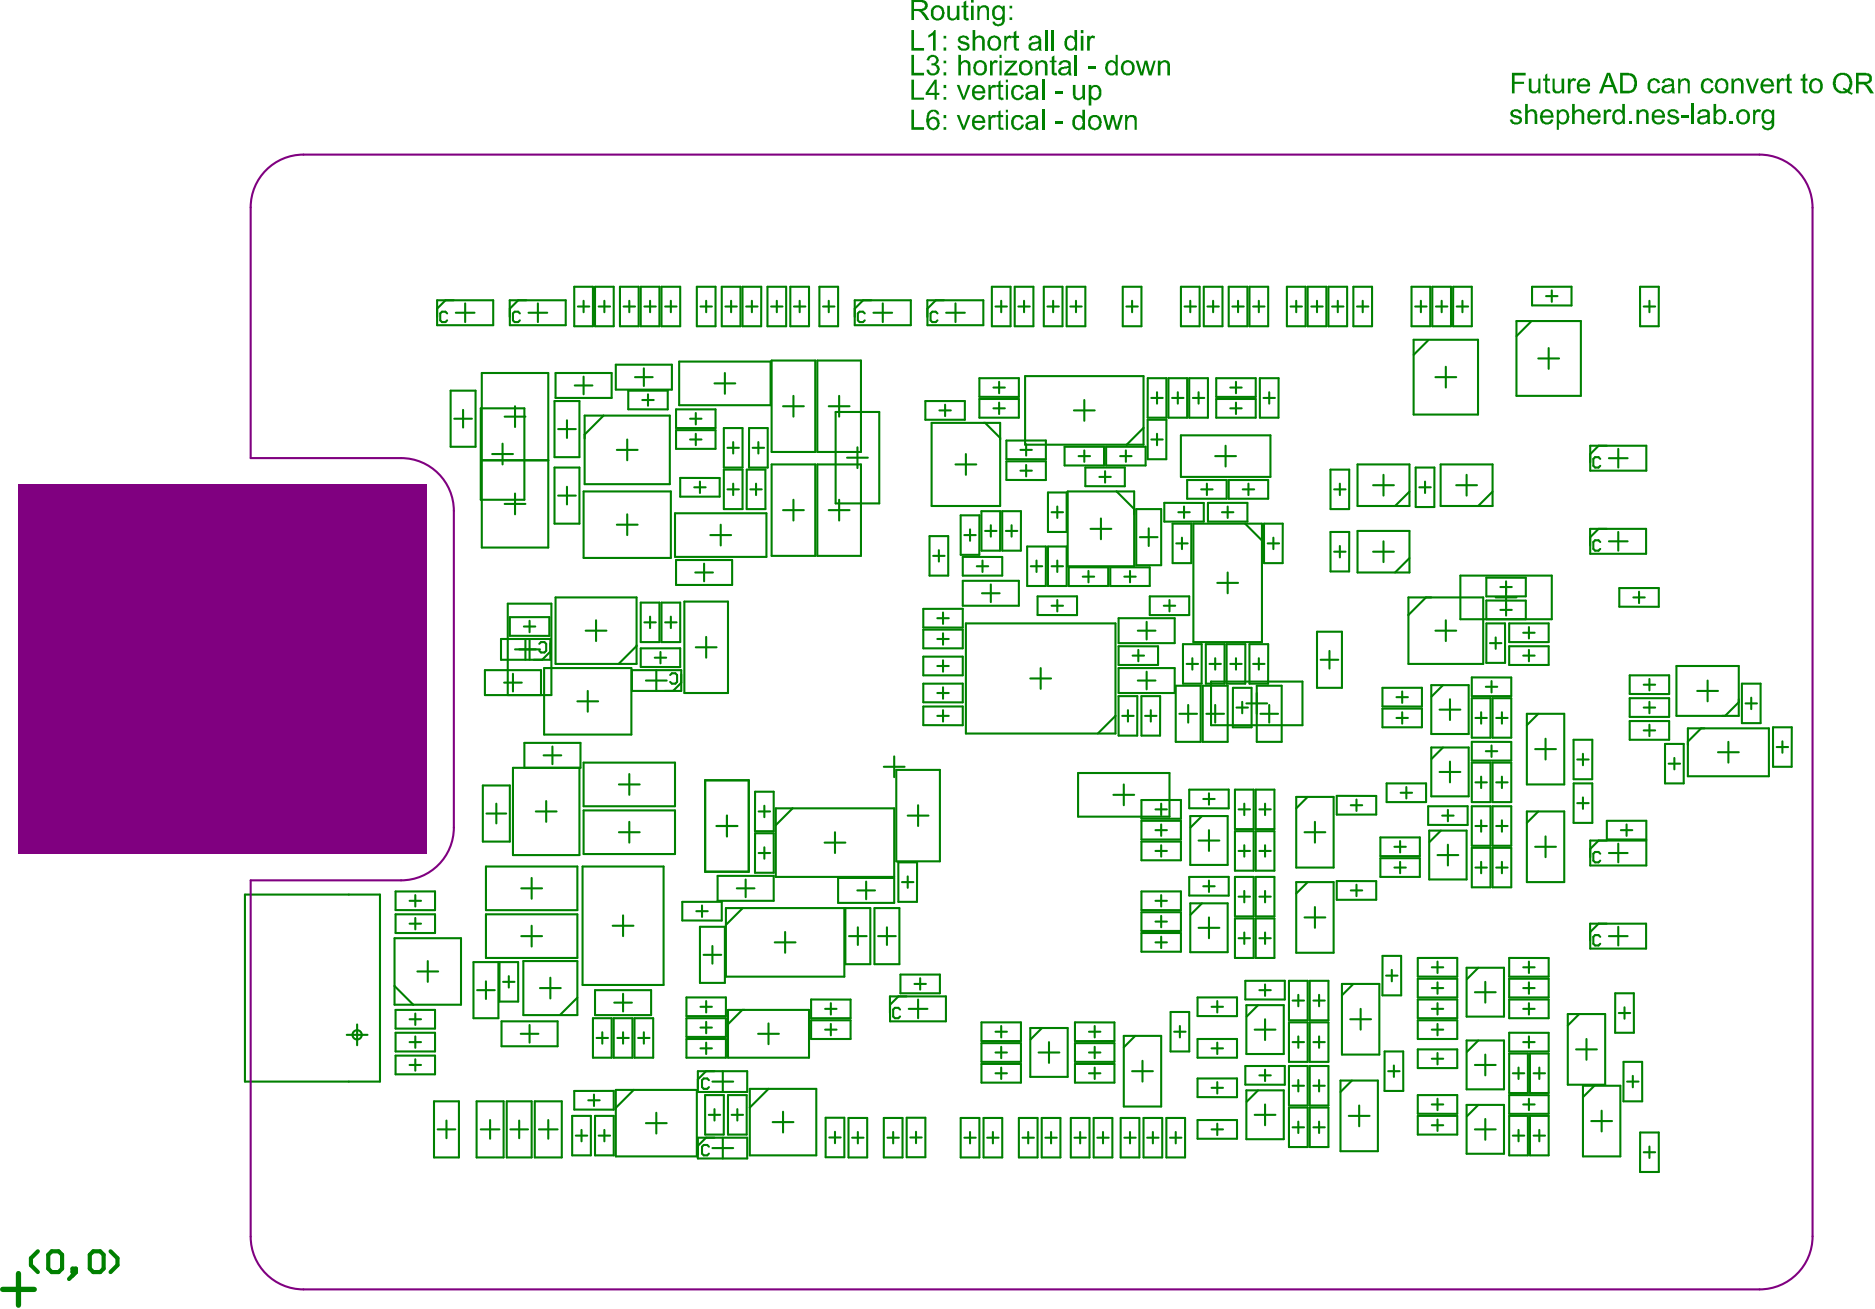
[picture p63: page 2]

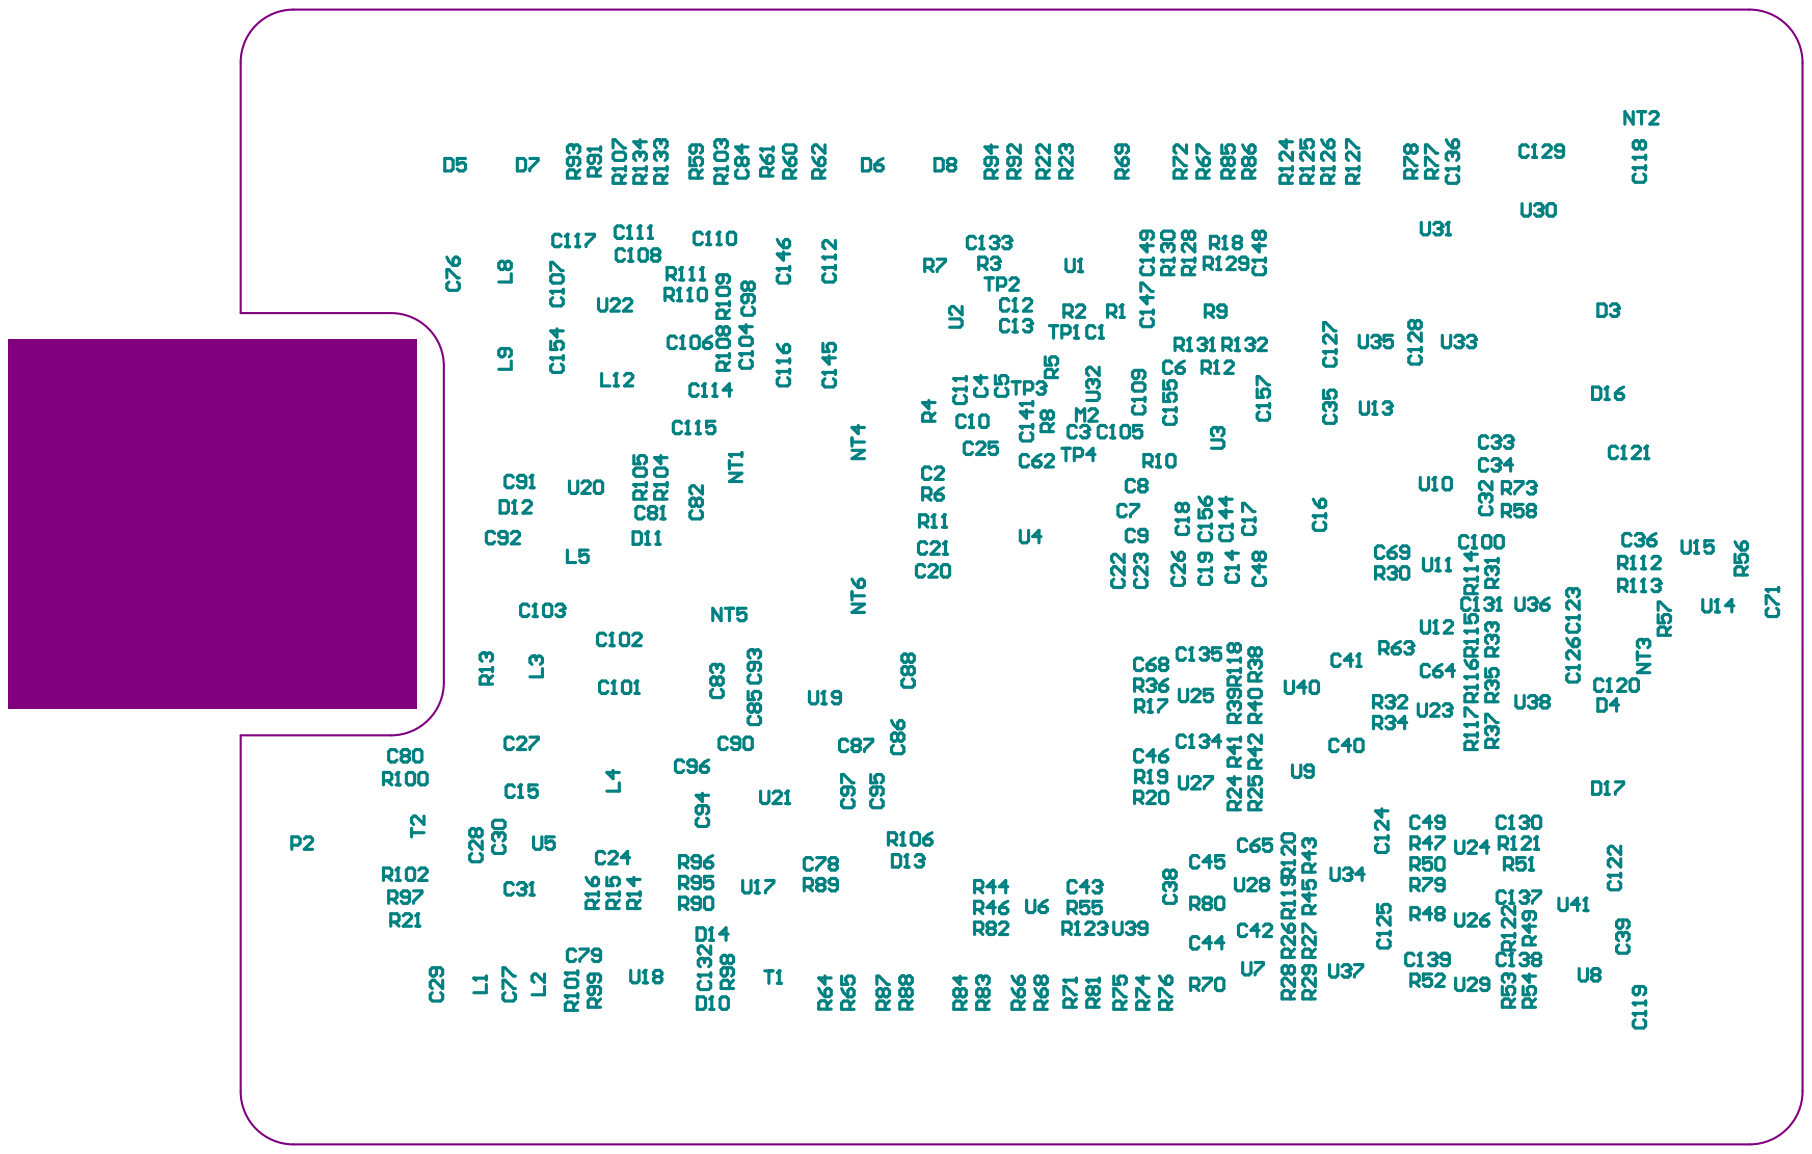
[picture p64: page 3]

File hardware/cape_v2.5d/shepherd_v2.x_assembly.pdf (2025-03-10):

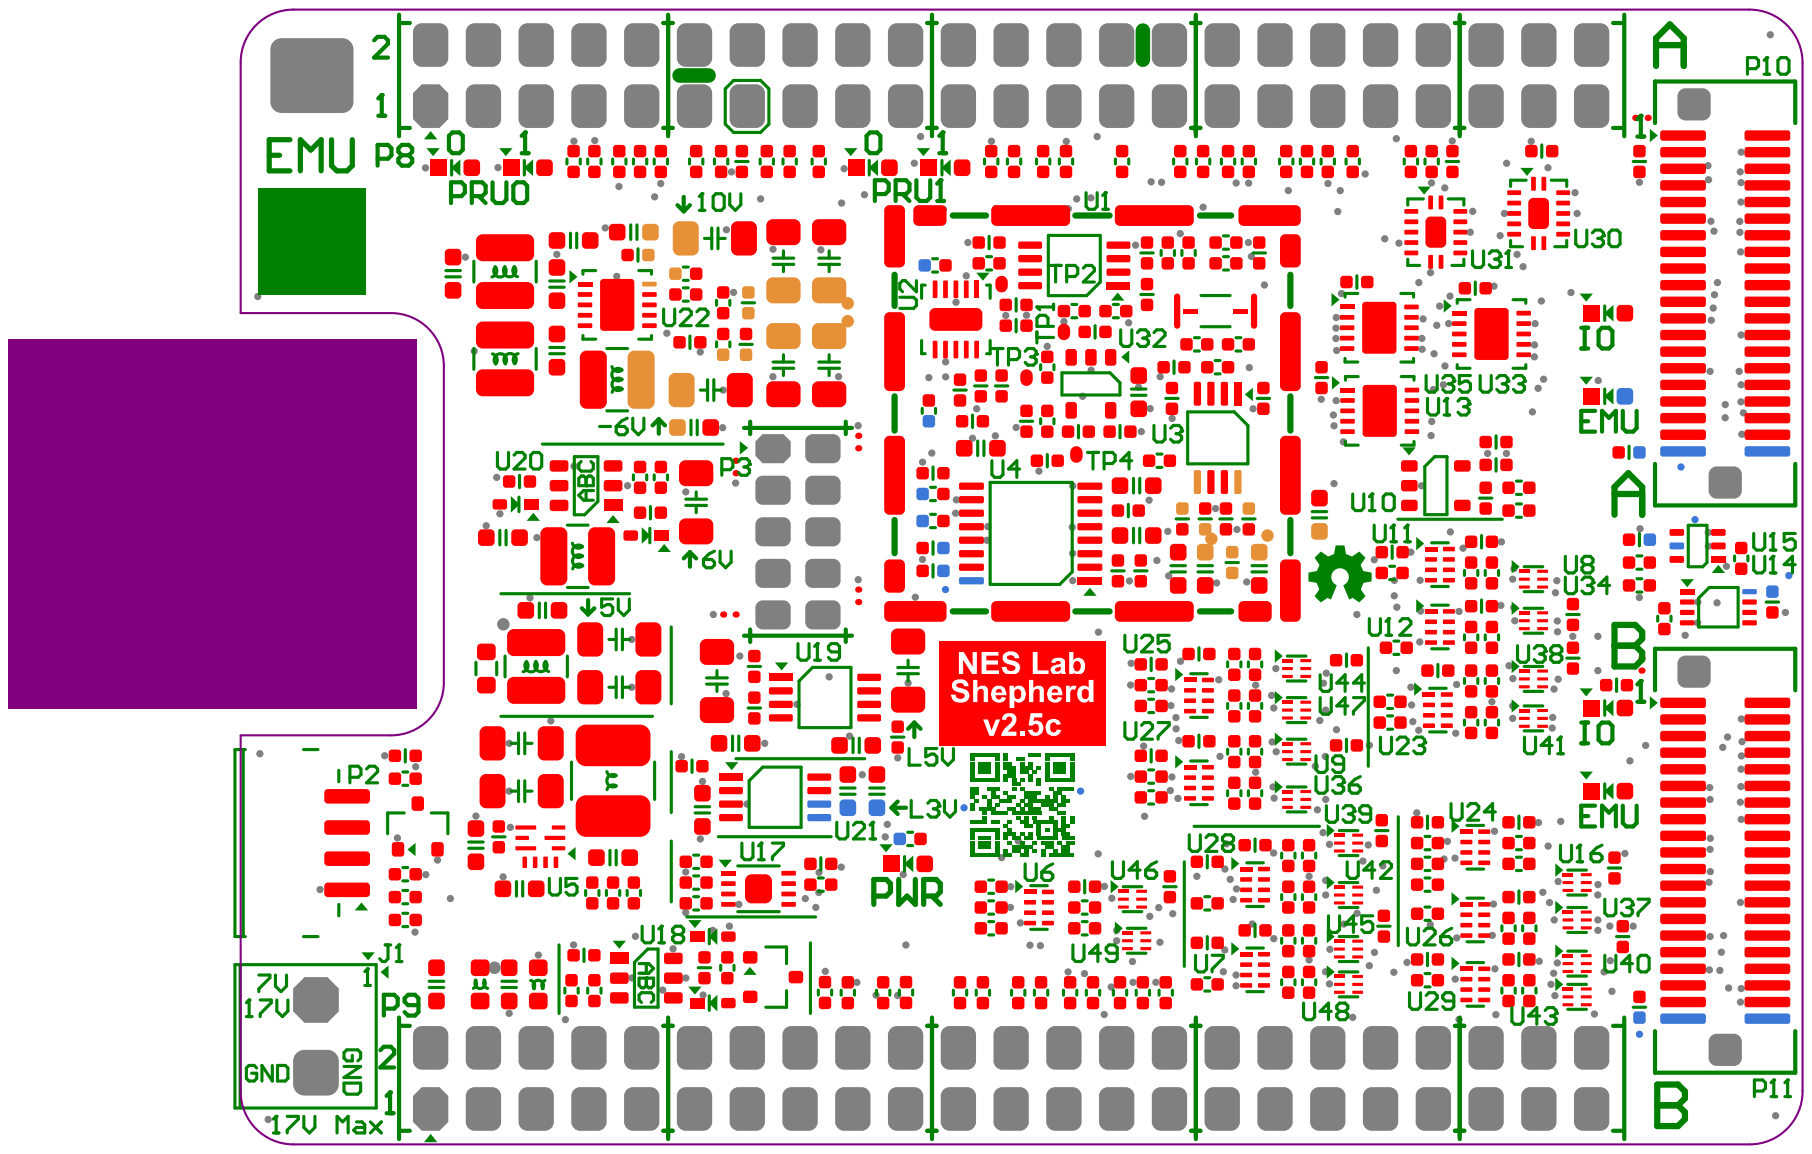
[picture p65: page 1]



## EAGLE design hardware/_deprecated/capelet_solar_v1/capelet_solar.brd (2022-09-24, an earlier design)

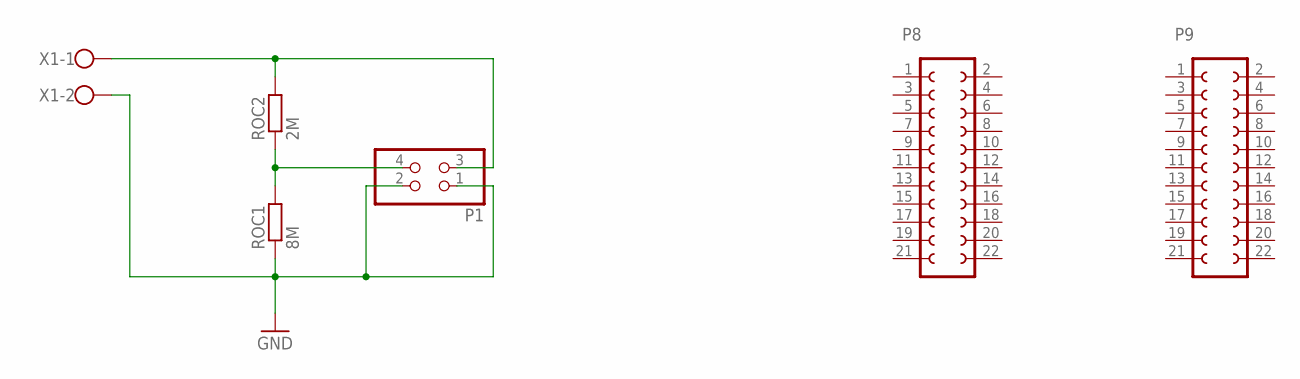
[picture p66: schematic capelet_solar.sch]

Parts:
P1: PINHD-2X2; 2X02
P8, P9: FE11-2
ROC1: 8M; RESC2012X65
ROC2: 2M; RESC2012X65
X1: W237-102

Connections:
GND: P1.1, P1.2, ROC1.1, X1.2
unnamed: P1.3, ROC2.2, X1.1
unnamed: P1.4, ROC1.2, ROC2.1

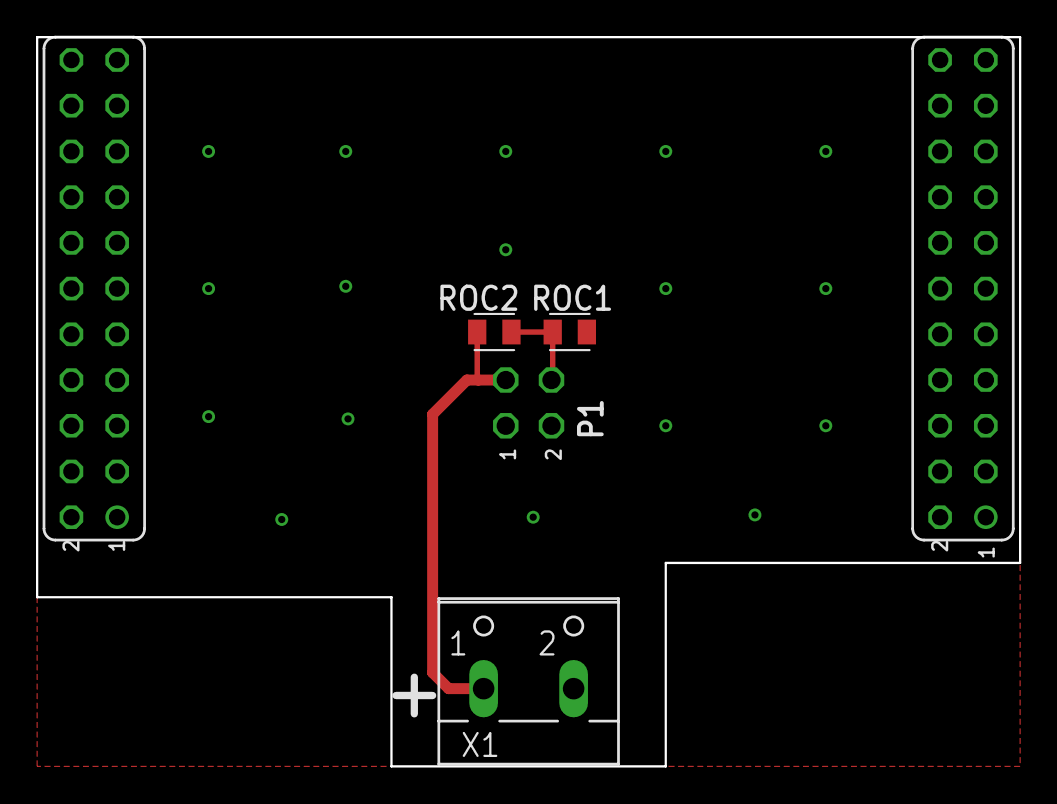
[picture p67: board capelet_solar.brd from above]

Board: 2 copper layers, 54.6 x 40.5 mm, 7 parts (1 on the bottom side), 3 nets.

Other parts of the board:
U$1: SHPRD_CPLT_H

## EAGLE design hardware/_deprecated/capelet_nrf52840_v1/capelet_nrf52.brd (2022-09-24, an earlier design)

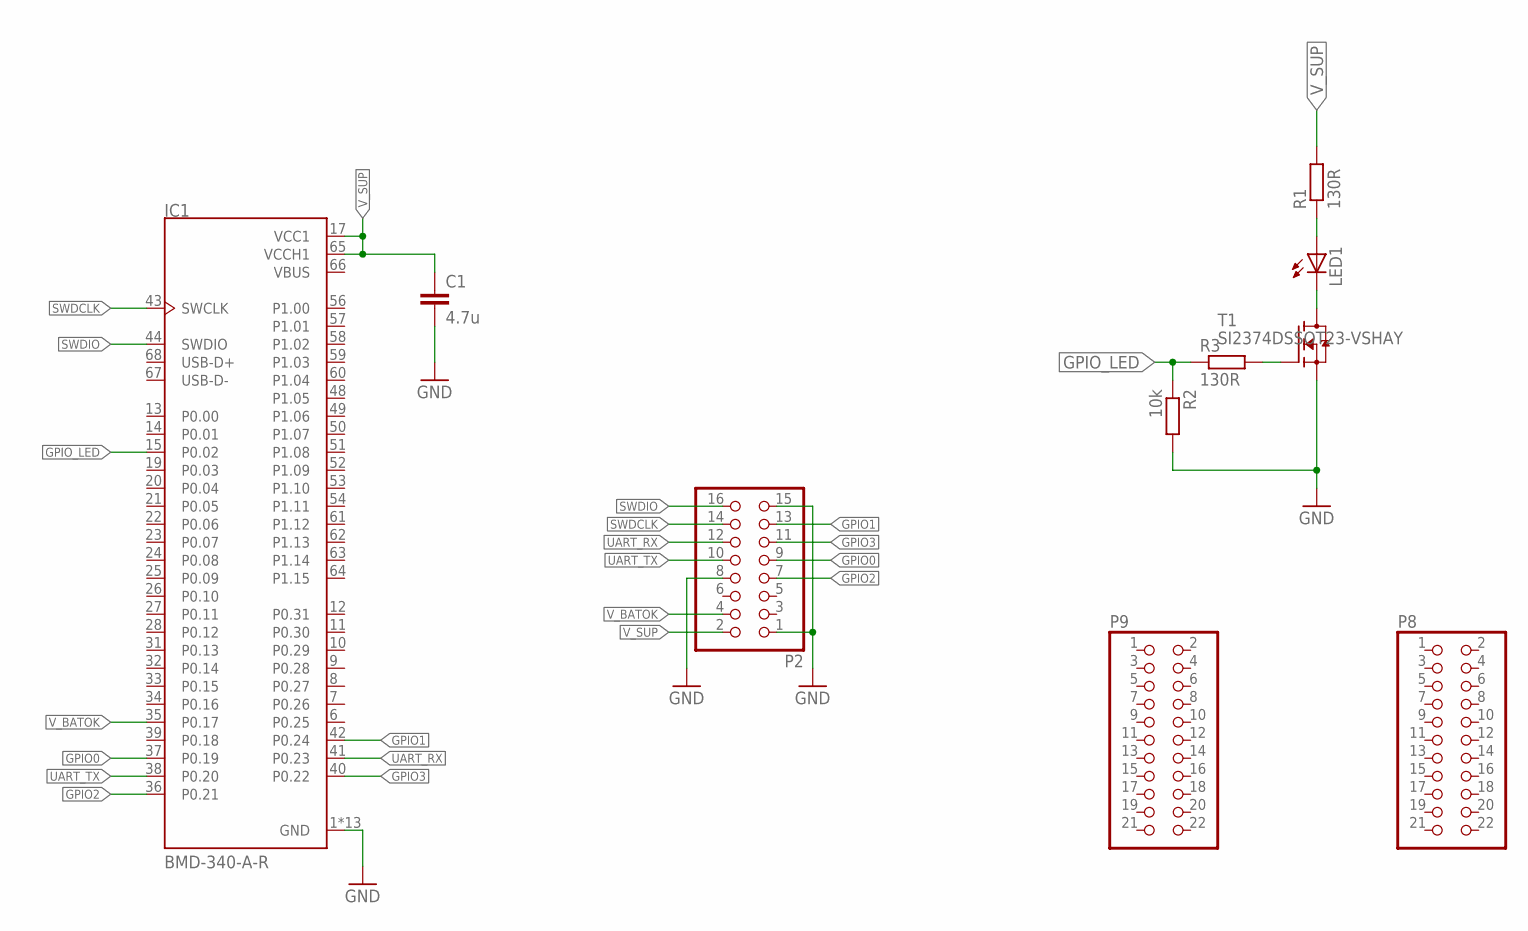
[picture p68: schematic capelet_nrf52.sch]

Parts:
C1: 4.7u; CAPC1608X95
IC1: BMD-340-A-R; RIGADO_BMD-340-A-R
LED1: 598-8130-107FLED_0805; LEDC2012X75
P2: PINHD-2X8; 2X08
P8, P9: PINHD-2X11; 2X11
R1, R3: 130R; RESC2012X65
R2: 10k; RESC2012X65
T1: SI2374DSSOT23-VSHAY; SOT95P237X112-3

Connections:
GND: C1.2, IC1.1 (GND), IC1.2 (GND), IC1.3 (GND), IC1.4 (GND), IC1.5 (GND), IC1.16 (GND), IC1.18 (GND), IC1.29 (GND), IC1.30 (GND), IC1.45 (GND), IC1.46 (GND), IC1.47 (GND), IC1.55 (GND), P2.1, P2.8, P2.15, R2.2, T1.2 (S)
GPIO0: IC1.37 (P0.19), P2.9
GPIO1: IC1.42 (P0.24), P2.13
GPIO2: IC1.36 (P0.21), P2.7
GPIO3: IC1.40 (P0.22), P2.11
GPIO_LED: IC1.15 (P0.02), R2.1, R3.1
unnamed: R3.2, T1.1 (G)
unnamed: LED1.1 (C), T1.3 (D)
unnamed: LED1.2 (A), R1.1
SWDCLK: IC1.43 (SWCLK), P2.14
SWDIO: IC1.44 (SWDIO), P2.16
UART_RX: IC1.41 (P0.23), P2.12
UART_TX: IC1.38 (P0.20), P2.10
VBUS: IC1.66 (VBUS)
V_BATOK: IC1.35 (P0.17), P2.4
V_SUP: C1.1, IC1.17 (VCC1), IC1.65 (VCCH1), P2.2, R1.2

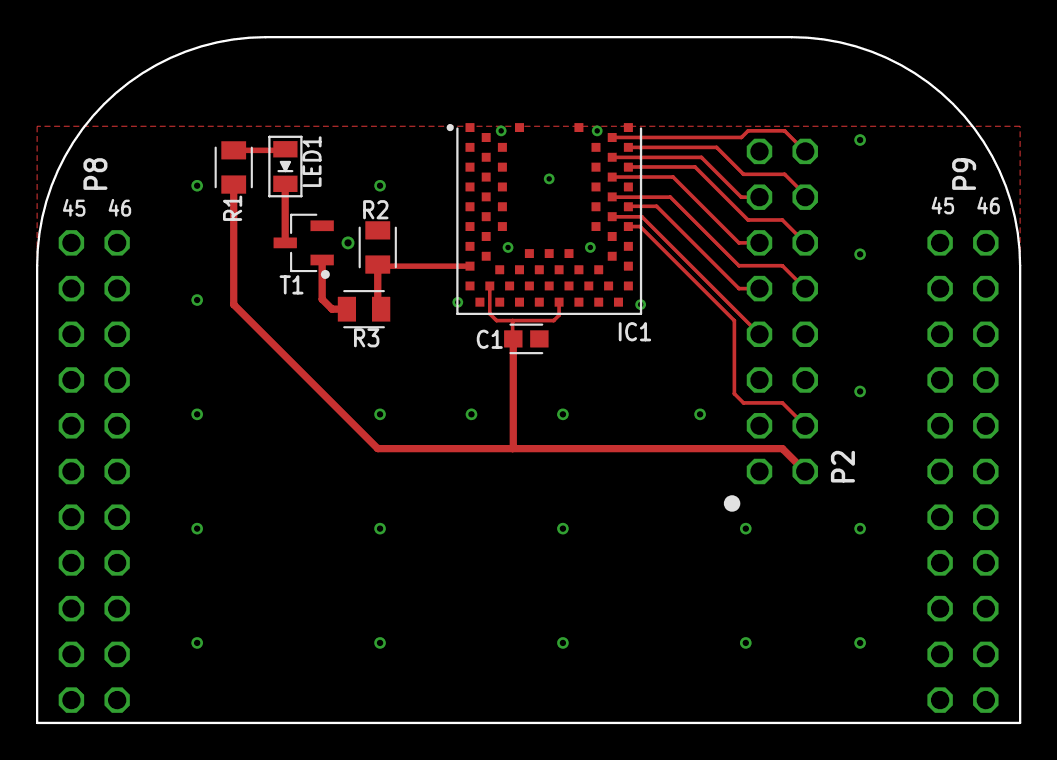
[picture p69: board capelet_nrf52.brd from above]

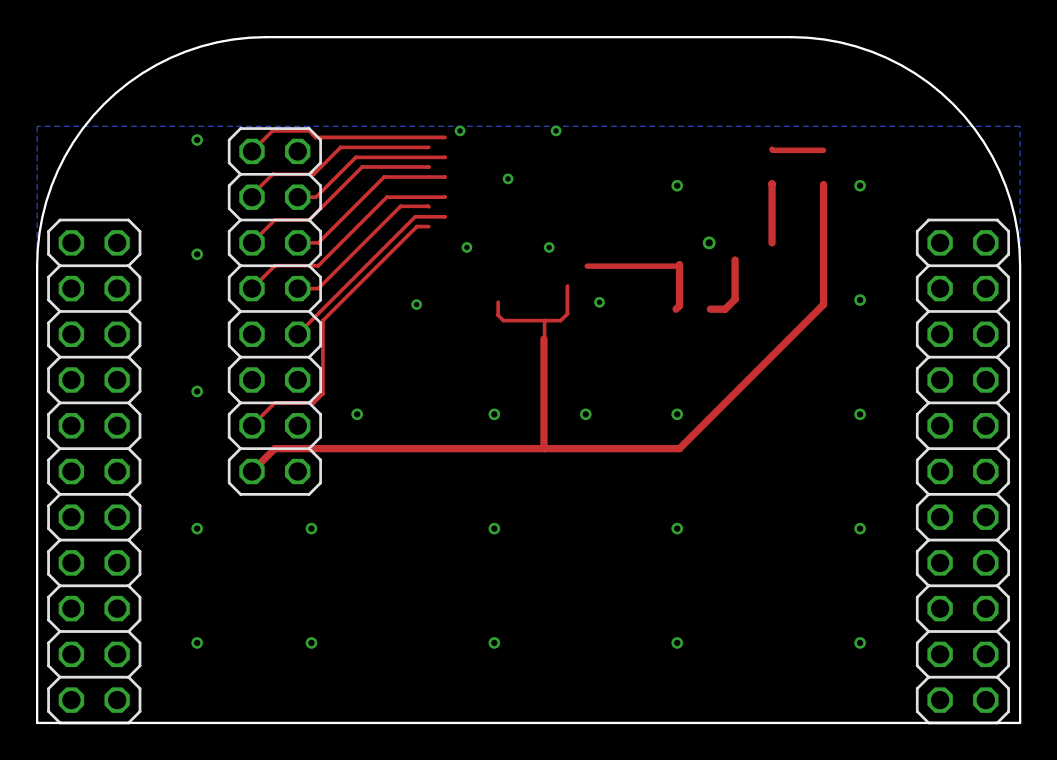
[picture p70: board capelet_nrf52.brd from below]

Board: 2 copper layers, 54.6 x 38.1 mm, 11 parts (3 on the bottom side), 15 nets.

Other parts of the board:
U$3: SHPRD_CPLT_T

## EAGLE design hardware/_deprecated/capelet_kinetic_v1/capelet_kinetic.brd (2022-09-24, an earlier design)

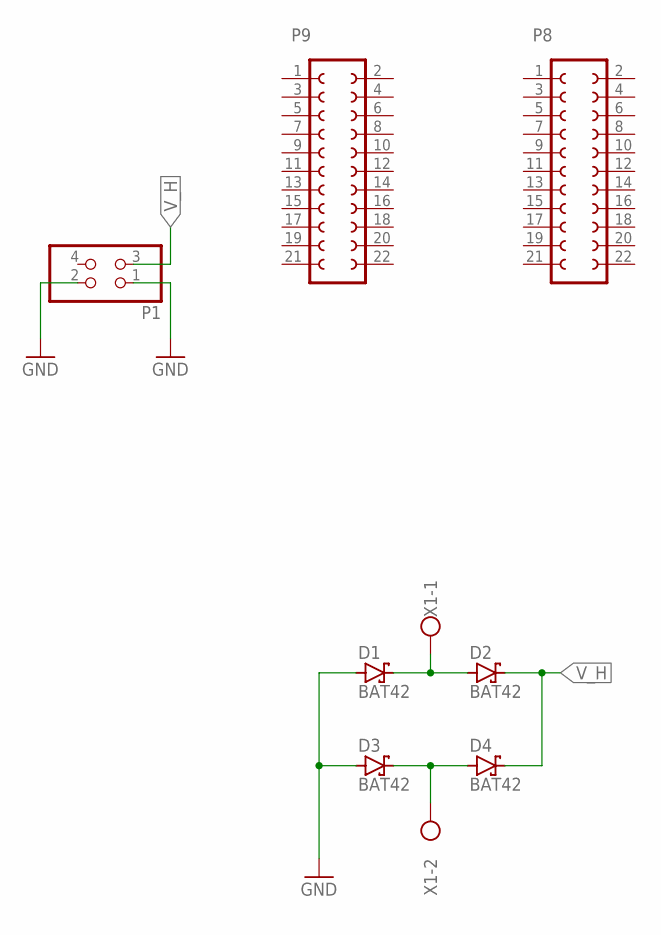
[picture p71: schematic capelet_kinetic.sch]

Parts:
D1, D2, D3, D4: BAT42; DO35-10
P1: PINHD-2X2; 2X02
P8, P9: FE11-2
X1: W237-102

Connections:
GND: D1.A, D3.A, P1.1, P1.2
unnamed: D1.C, D2.A, X1.1
unnamed: D3.C, D4.A, X1.2
V_H: D2.C, D4.C, P1.3

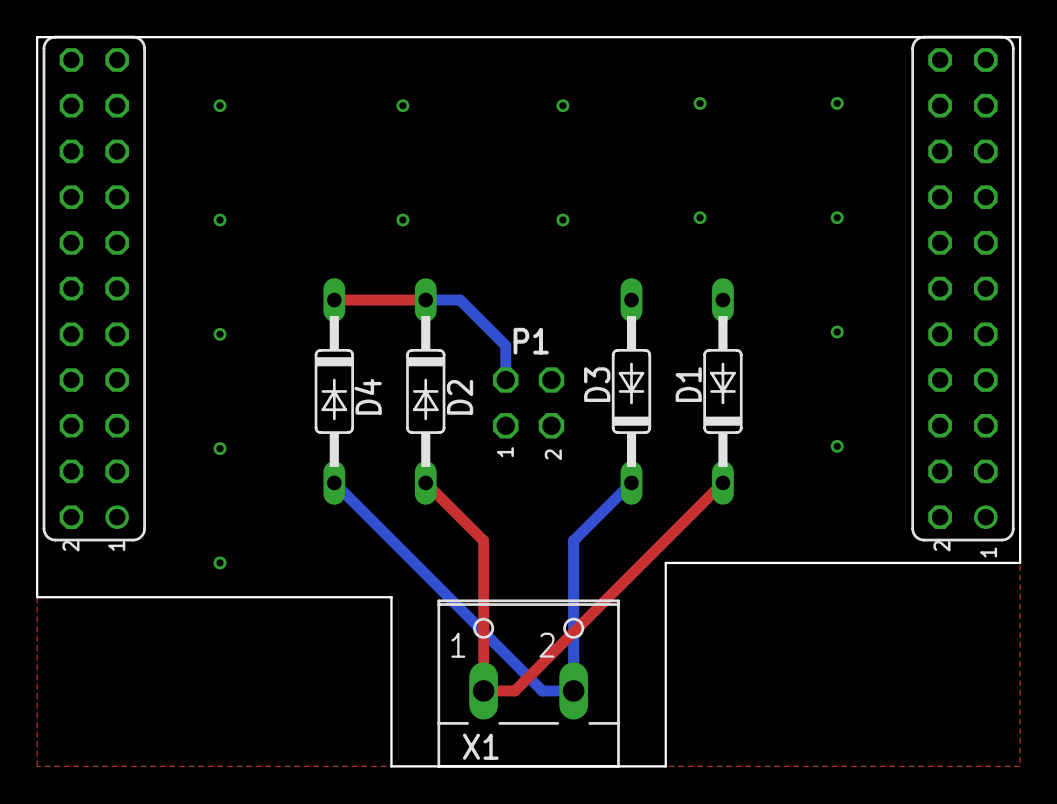
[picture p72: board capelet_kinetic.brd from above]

Board: 2 copper layers, 54.6 x 40.5 mm, 9 parts (1 on the bottom side), 4 nets.

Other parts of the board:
U$1: SHPRD_CPLT_H

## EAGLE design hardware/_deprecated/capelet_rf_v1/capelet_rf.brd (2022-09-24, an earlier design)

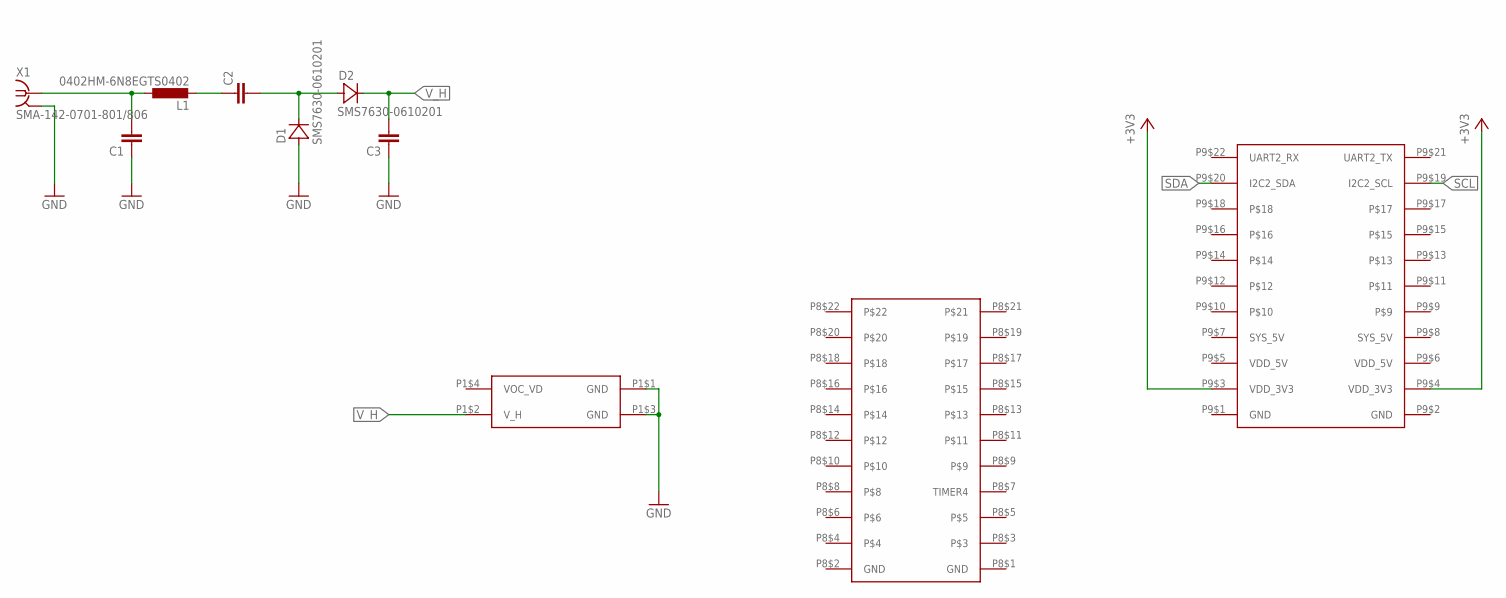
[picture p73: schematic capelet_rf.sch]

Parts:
C1, C2, C3: C_SMD0402; CAPC1005X55
D1, D2: SMS7630-0610201; DIOC0502X27N
L1: 0402HM-6N8EGTS0402; INDC1004X60N
X1: SMA-142-0701-801/806; J502-ND-142-0701-801/806
Y1: SHPRD_CPLT_H

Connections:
+3V3: Y1.P9$3 (VDD_3V3), Y1.P9$4 (VDD_3V3)
GND: C1.1, C3.1, D1.1 (A), X1.G@1 (2), X1.G@2 (2), X1.G@3 (2), X1.G@4 (2), Y1.P1$1 (GND), Y1.P1$3 (GND), Y1.P8$1 (GND), Y1.P8$2 (GND), Y1.P9$1 (GND), Y1.P9$2 (GND)
unnamed: C2.2, D1.2 (C), D2.1 (A)
unnamed: C1.2, L1.1, X1.1
unnamed: C2.1, L1.2
SCL: Y1.P9$19 (I2C2_SCL)
SDA: Y1.P9$20 (I2C2_SDA)
SYS_5V: Y1.P9$7 (SYS_5V), Y1.P9$8 (SYS_5V)
VDD_5V: Y1.P9$5 (VDD_5V), Y1.P9$6 (VDD_5V)
V_H: C3.2, D2.2 (C), Y1.P1$2 (V_H)

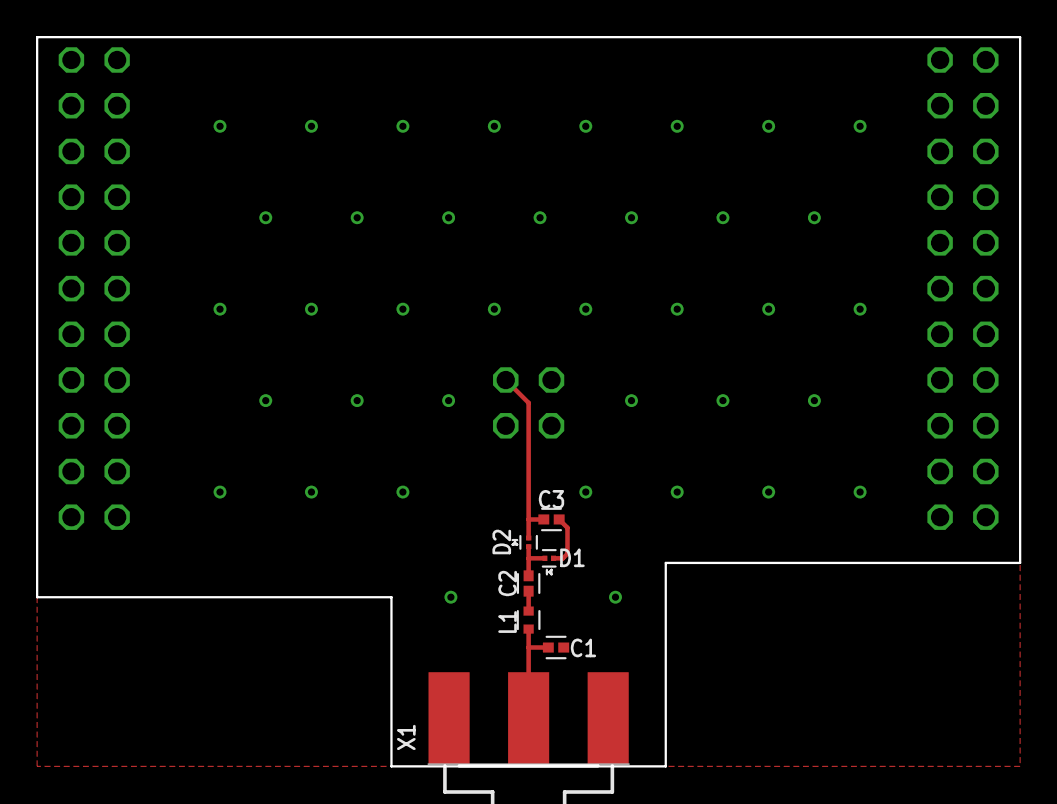
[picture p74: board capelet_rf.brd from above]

Board: 2 copper layers, 54.6 x 40.5 mm, 8 parts (0 on the bottom side), 8 nets.

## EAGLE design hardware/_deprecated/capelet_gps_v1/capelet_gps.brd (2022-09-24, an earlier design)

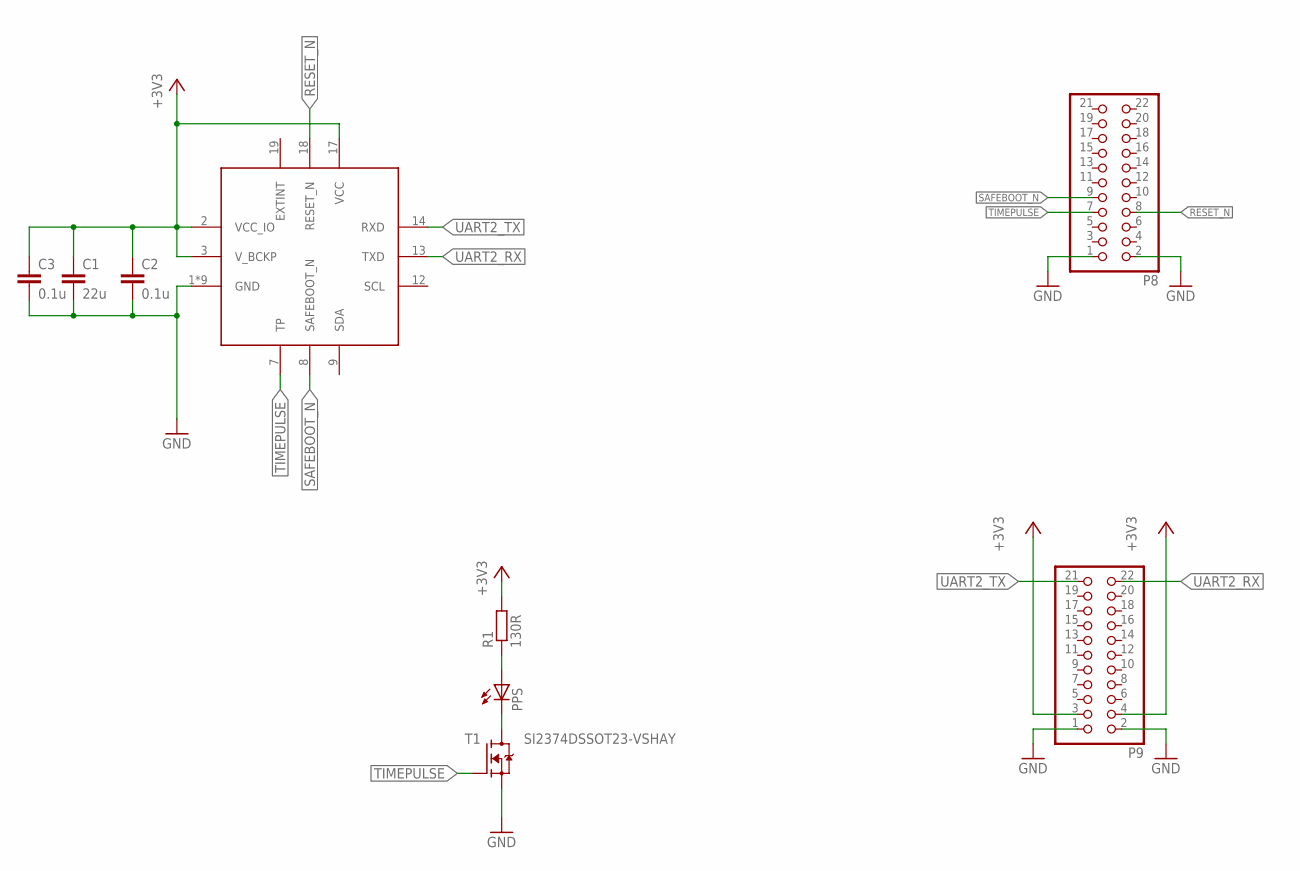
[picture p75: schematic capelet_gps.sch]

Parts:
C1: 22u; CAPC3225X280
C2, C3: 0.1u; CAPC2012X145
IC1: SAM-M8Q
P8, P9: PINHD-2X11; 2X11
PPS: 598-8130-107FLED_0805; LEDC2012X75
R1: 130R; RESC2012X65
T1: SI2374DSSOT23-VSHAY; SOT95P237X112-3

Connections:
+3V3: C1.1, C2.1, C3.1, IC1.2 (VCC_IO), IC1.3 (V_BCKP), IC1.17 (VCC), P9.3 (4), P9.4 (3), R1.2
GND: C1.2, C2.2, C3.2, IC1.1 (GND), IC1.4 (GND), IC1.5 (GND), IC1.6 (GND), IC1.10 (GND), IC1.11 (GND), IC1.15 (GND), IC1.16 (GND), IC1.20 (GND), P8.1 (2), P8.2 (1), P9.1 (2), P9.2 (1), T1.2 (S)
unnamed: PPS.1 (C), T1.3 (D)
unnamed: PPS.2 (A), R1.1
RESET_N: IC1.18 (RESET_N), P8.8 (7)
SAFEBOOT_N: IC1.8 (SAFEBOOT_N), P8.9 (10)
TIMEPULSE: IC1.7 (TP), P8.7 (8), T1.1 (G)
UART2_RX: IC1.13 (TXD), P9.22 (21)
UART2_TX: IC1.14 (RXD), P9.21 (22)

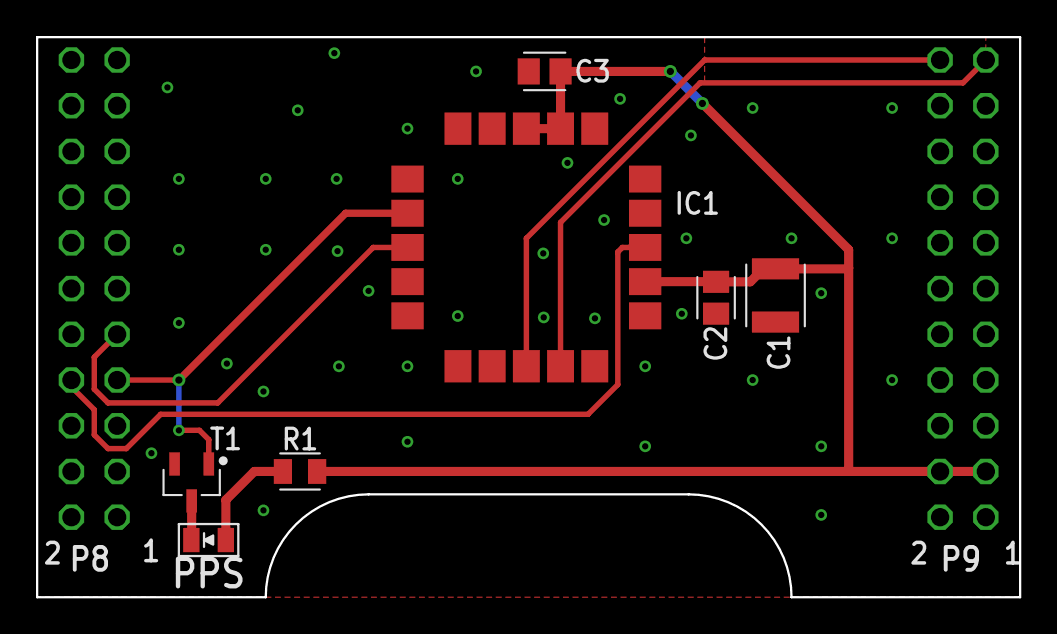
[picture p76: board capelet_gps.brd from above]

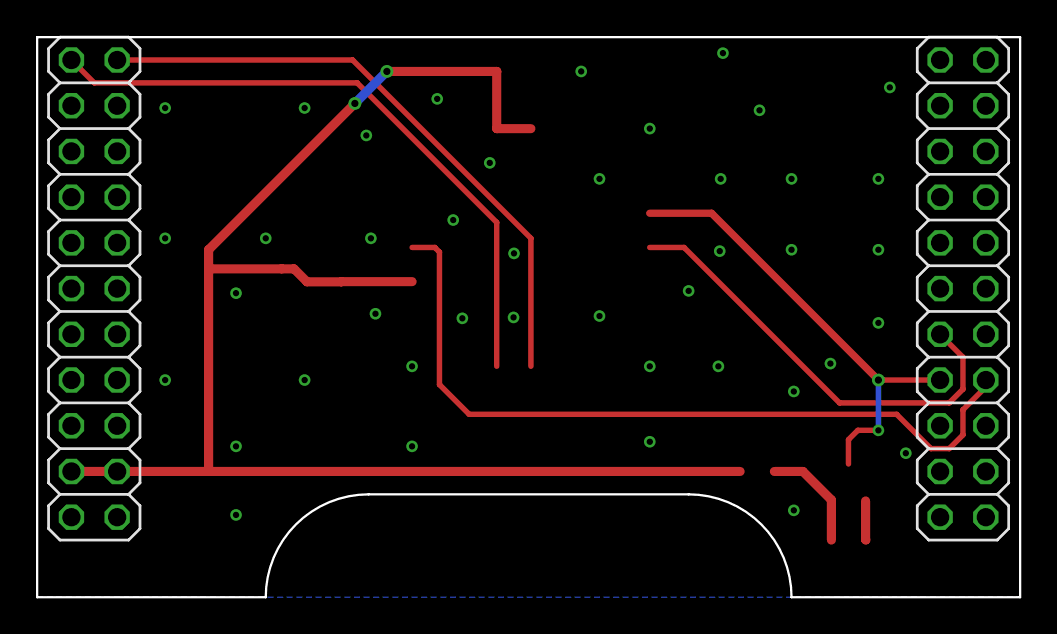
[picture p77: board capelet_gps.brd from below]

Board: 2 copper layers, 54.6 x 31.1 mm, 13 parts (2 on the bottom side), 9 nets.

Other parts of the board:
U$1, U$2, U$4: REFMARK
U$3: SHPRD_CPLT_G

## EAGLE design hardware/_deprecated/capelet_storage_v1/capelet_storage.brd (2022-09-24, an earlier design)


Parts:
C1: C_SMD0805; CAPC2012X145
C2: C_SMD1210; CAPC3225X280
C3: CPOL-EUE5-8.5; E5-8,5
P3, P4: PINHD-1X4; 1X04

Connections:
+3V3: P3.1
GND: C1.2, C2.2, C3.-, P3.3, P3.4, P4.1, P4.2, P4.3, P4.4
unnamed: C1.1, C2.1, C3.+, P3.2



Board: 2 copper layers, 16.5 x 12.7 mm, 6 parts (2 on the bottom side), 2 nets.

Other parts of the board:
U$1: SHPRD_CPLT_S

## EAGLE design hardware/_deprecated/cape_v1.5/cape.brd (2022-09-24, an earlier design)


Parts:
C7, C8: 0.1u; CAPC1005X55
IC3: AD8422BRMZ; RM_8-L
JP2: PINHD-1X2; 1X02
R10: 220; RESC1608X55
R11: 2; RESC1608X55
R12: 402; RESC1608X55
S3: G3VM-31HR22SOP; SOP06
T2: SI2374DSSOT23-VSHAY; SOT95P237X112-3

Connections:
+3V3: R10.2; also elsewhere on the board
EN_HRVST: T2.1 (G); also elsewhere on the board
GND: C7.2, C8.2, IC3.6 (REF), T2.2 (S); also elsewhere on the board
unnamed: R10.1, S3.1 (A)
unnamed: IC3.3 (RG_2), R12.2
unnamed: IC3.2 (RG), R12.1
unnamed: S3.2 (K), T2.3 (D)
VDD: C8.1, IC3.8 (V+); also elsewhere on the board
VSS: C7.1, IC3.5 (V-); also elsewhere on the board
V_AIN: IC3.7 (OUT); also elsewhere on the board
V_BQ: JP2.1; also elsewhere on the board
V_H: S3.4 (D2); also elsewhere on the board
V_IN_SHT+: IC3.4 (IN+), R11.2, S3.6 (D1); also elsewhere on the board
V_IN_SHT-: IC3.1 (IN-), JP2.2, R11.1; also elsewhere on the board

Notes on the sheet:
V_LED=1.33, I_LED=0.01
GAIN=50.25
Harvesting current recorder (Shunt Amperemeter with precision instrumentation amplifier)
Low on-res switch for connecting/disconnecting harvester
Jumper to enable tapping into current path for calibration


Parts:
C1, C2, C3: 0.1u; CAPC1005X55
C4, C5: 1n; CAPC1005X55
IC1: AD8422BRMZ; RM_8-L
IC2: OPA2388DGK8_L; DGK8-L
JP1: PINHD-1X2; 1X02
LED3, LED4: 598-8130-107FLED_0805; LEDC2012X75
R1: 402; RESC1608X55
R2: 2; RESC1608X55
R3: 24; RESC1005X40
R4: 2.4k; RESC1005X40
R5: 3.6k; RESC1005X40
R6, R7: 10k; RESC1005X40
R8: 1.2k; RESC1005X40
R9: 91; RESC1608X55
S1: ADG849YKSZ-REELKS_6-L; KS_6-L
T1: SI2374DSSOT23-VSHAY; SOT95P237X112-3

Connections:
+3V3: C1.1, IC2.8 (V+), R5.1; also elsewhere on the board
GND: C1.2, C2.2, C3.2, IC1.6 (REF), IC2.4 (V-), R6.2, S1.3 (GND), T1.2 (S); also elsewhere on the board
unnamed: R8.1, T1.1 (G)
unnamed: LED3.2 (A), LED4.2 (A), R9.1
unnamed: C5.2, IC2.1 (OUT), R7.1, R8.2
unnamed: LED3.1 (C), LED4.1 (C), T1.3 (D)
unnamed: C5.1, IC2.3 (IN+), R4.2, R7.2
unnamed: IC2.2 (IN-), R5.2, R6.1
unnamed: C4.1, IC2.6 (IN-), R3.1, R4.1
unnamed: C4.2, IC2.7 (OUT), R3.2
unnamed: IC1.2 (RG), R1.2
unnamed: IC1.3 (RG_2), R1.1
SLCT_LOAD: S1.1 (IN); also elsewhere on the board
VDD: C2.1, IC1.8 (V+), S1.2 (VDD); also elsewhere on the board
VSS: C3.1, IC1.5 (V-); also elsewhere on the board
V_AOUT: IC1.7 (OUT); also elsewhere on the board
V_LD_SHT+: IC1.4 (IN+), JP1.2, R2.2; also elsewhere on the board
V_LOAD: IC1.1 (IN-), R2.1, S1.5 (D); also elsewhere on the board
V_STR: JP1.1; also elsewhere on the board
V_SUP_DUMMY: IC2.5 (IN+), R9.2, S1.4 (S1)
V_SUP_TARGET: S1.6 (S2); also elsewhere on the board

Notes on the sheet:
IN low: D--S1
GAIN=50.25
V_REF=2.426V
V_ON=3.008V V_OFF=2.216
Dummy Load: consumes the energy stored on the capacitor during recording. It switches two LEDs on when the cap voltage reaches V_ON and switches them off when voltage decreases to V_OFF.
Voltage buffer
Schmitt-Trigger
Switch for switching between dummy (for recording) and target (for emulation) load
Load current recorder (shunt Amperemeter with precision instrumentation amplifier)
Jumper to enable tapping into current path for calibration


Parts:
C12, C13, C18, C21: 10u; CAPC2012X145
C14, C15, C16, C19, C20, C22: 1u; CAPC1608X95
C17: 22u; CAPC3225X280
C23: 0.1u; CAPC1005X55
C24, C25: 1n; CAPC1005X55
IC5: ADS8694TSSOP38; TSSOP38
IC6: OPA2388DGK8_L; DGK8-L
R20, R21: 24; RESC1005X40
TP3, TP4: TPSQTP06R; TP06R

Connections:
+3V3: C21.1, C22.1, IC5.34 (DVDD); also elsewhere on the board
CS_ADC: IC5.38 (CS_N); also elsewhere on the board
GND: C12.2, C13.2, C14.2, C15.2, C16.2, C17.2, C18.2, C19.2, C20.2, C21.2, C22.2, C23.2, IC5.3 (DAISY), IC5.4 (REFSEL_N), IC5.6 (REFGND), IC5.8 (AGND), IC5.17 (AIN_0GND), IC5.19 (AIN_1GND), IC5.20 (AIN2_GND), IC5.22 (AIN_3GND), IC5.28 (AGND_2), IC5.29 (AGND_3), IC5.31 (AGND_4), IC5.32 (AGND_5), IC5.33 (DGND), IC6.4 (V-); also elsewhere on the board
MISO: IC5.36 (SDO); also elsewhere on the board
MOSI: IC5.1 (SDI); also elsewhere on the board
unnamed: C13.1, IC5.5 (REFIO)
unnamed: C15.1, C17.1, IC5.7 (REFCAP)
unnamed: IC5.10 (AUX_IN), IC5.11 (AUX_GND)
unnamed: C25.2, IC6.1 (OUT), R21.1
unnamed: C24.2, IC6.7 (OUT), R20.1
RST/PDN_ADC: IC5.2 (RST_PD_N); also elsewhere on the board
SCLK: IC5.37 (SCLK); also elsewhere on the board
VDD: C12.1, C14.1, C16.1, C18.1, C19.1, C20.1, C23.1, IC5.9 (AVDD), IC5.30 (AVDD_2), IC6.8 (V+); also elsewhere on the board
V_AIN: IC5.21 (AIN_2P), TP4.TP; also elsewhere on the board
V_AOUT: IC5.23 (AIN_3P), TP3.TP; also elsewhere on the board
V_IN_SHT-: IC6.5 (IN+); also elsewhere on the board
V_LOAD: IC6.3 (IN+); also elsewhere on the board
V_VIN: C24.1, IC5.16 (AIN_0P), IC6.6 (IN-), R20.2
V_VOUT: C25.1, IC5.18 (AIN_1P), IC6.2 (IN-), R21.2

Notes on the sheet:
REFSEL low: internal reference
DAISY on GND: stand-alone mode
ADC for all 4 channels (harvesting/load current/voltage)
Voltage buffer for two voltage channels


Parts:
C6, C30, C31: 0.1u; CAPC1005X55
C9, C29, C33, C34: 1n; CAPC1005X55
C10: 2.2n; CAPC1005X55
C11: 10u; CAPC2012X145
C32, C35: 1u; CAPC1608X95
D1: BAT43WS-HE3SOD-323; SOD2513X110
IC4: OPA2388DGK8_L; DGK8-L
IC9: LMP7701MF; DBV5-L
IC10: DAC8562_DGS_10; DGS10
R13, R18: 220; RESC1608X55
R14, R17, R31: 10k; RESC1005X40
R15: 402; RESC1608X55
R16, R28, R30: 1.2k; RESC1005X40
R19: 30; RESC1005X40
R27, R29: 100k; RESC1005X40
T3: SI2374DSSOT23-VSHAY; SOT95P237X112-3
T4: SI2307SOT23-VSHAY; SOT95P237X112-3
TP1, TP2: TPSQTP06R; TP06R

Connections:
CS_DAC: IC10.6 (!SYNC); also elsewhere on the board
GND: C6.2, C11.2, C30.2, C31.2, C32.2, C33.2, C34.2, C35.2, IC4.4 (V-), IC10.3 (GND), IC10.4 (!LDAC), R16.2, R29.2; also elsewhere on the board
MOSI: IC10.8 (DIN); also elsewhere on the board
unnamed: C9.2, IC4.1 (OUT), R13.2
unnamed: C9.1, IC4.2 (IN-), R14.2
unnamed: IC10.5 (!CLR), R31.2
unnamed: D1.2 (A), T4.3 (D)
unnamed: C29.1, IC9.4 (IN-), R27.1, R30.2
unnamed: IC9.3 (IN+), R28.1, R29.1
unnamed: R13.1, T3.1 (G)
unnamed: R14.1, R16.1, T3.2 (S), TP1.TP
unnamed: IC4.5 (IN+), R15.2, T3.3 (D)
unnamed: C10.1, IC4.6 (IN-), R17.2
unnamed: C10.2, IC4.7 (OUT), R18.2
unnamed: R18.1, T4.1 (G)
unnamed: R17.1, R19.2, T4.2 (S), TP2.TP
SCLK: IC10.7 (SCLK); also elsewhere on the board
VDD: C6.1, C11.1, C31.1, C32.1, C33.1, C34.1, IC4.8 (V+), IC9.5 (V+), IC10.9 (AVDD), R15.1, R19.1, R31.1; also elsewhere on the board
VSS: C30.1, IC9.2 (V-); also elsewhere on the board
V_EMU_I: IC10.1 (VOUTA), R28.2
V_EMU_I_BIASED: C29.2, IC4.3 (IN+), IC9.1 (OUT), R30.1
V_EMU_V: IC10.2 (VOUTB); also elsewhere on the board
V_IN_SHT+: D1.1 (C); also elsewhere on the board
V_REF_2V5: C35.1, IC10.10 (VREFIN/VREFOUT), R27.2

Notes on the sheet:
Two channel DAC for generating reference voltages for emulation (I and V)
Subtractor for applying small negative bias to current emulation channel in order to guarantee zero output current
2mA@2.5V V_EMU_I_BIASED
804mV@2mA
26.8mA@0.804V
Precision V2I converter used as digitally controlled current source for emulation

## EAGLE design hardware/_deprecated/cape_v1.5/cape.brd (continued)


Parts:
D2: BZX384B5V1; SOD2513X110
J1: JST_S4B-ZR-SM4A-TFJST_S4B-ZR-SM4A-TF_0_0; JST_S4B-ZR-SM4A-TF_0
LED1, LED2: 598-8130-107FLED_0805; LEDC2012X75
P1: FE02-2
P2: FE08-2
P3, P4: FE04-1
P8, P9: FE23-2
R32, R33, R34, R35, R36, R37, R39, R40, R53: 510; RESC1005X40
R38, R41, R42: 220; RESC1608X55
R54: 10k; RESC1005X40
T5, T6, T7: SI2374DSSOT23-VSHAY; SOT95P237X112-3

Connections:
+3V3: J1.1, P2.5, P3.1, P9.3, P9.4, R41.2, R42.2, R54.1; also elsewhere on the board
+5V: P9.7, P9.8; also elsewhere on the board
BUTTON_LED_OD: J1.2, R38.2
CS_ADC: P9.25; also elsewhere on the board
CS_DAC: P9.31; also elsewhere on the board
EN_HRVST: R32.2; also elsewhere on the board
EN_LVLCNV: R37.1; also elsewhere on the board
EN_MPPT#: R34.2; also elsewhere on the board
EN_V_ANLG: R40.1; also elsewhere on the board
EN_V_FIX: P9.16, P9.29; also elsewhere on the board
GND: D2.2 (A), J1.4, J1.5 (MNT_1), J1.6 (MNT_2), P1.1, P1.3, P2.2, P2.7, P2.16, P3.3, P3.4, P4.1, P4.2, P4.3, P4.4, P8.1, P8.2, P9.1, P9.2, P9.43, P9.44, P9.45, P9.46, T5.2 (S), T6.2 (S), T7.2 (S); also elsewhere on the board
GPIO0_BB: P8.45; also elsewhere on the board
GPIO0_TARGET: P2.10; also elsewhere on the board
GPIO1_BB: P8.46; also elsewhere on the board
GPIO1_TARGET: P2.14; also elsewhere on the board
GPIO2_BB: P8.43; also elsewhere on the board
GPIO2_TARGET: P2.8; also elsewhere on the board
GPIO3_BB: P8.44; also elsewhere on the board
GPIO3_TARGET: P2.12; also elsewhere on the board
I2C1_SCL: P9.17; also elsewhere on the board
I2C1_SDA: P9.18; also elsewhere on the board
I2C2_SCL: P9.19; also elsewhere on the board
I2C2_SDA: P9.20; also elsewhere on the board
LED_BUTTON: R53.1, T7.1 (G)
LED_USR1: R35.1, T5.1 (G)
LED_USR2: R36.1, T6.1 (G)
MISO: P9.27; also elsewhere on the board
MOSI: P9.30; also elsewhere on the board
unnamed: LED1.1 (C), T5.3 (D)
unnamed: P8.13, R32.1
unnamed: P9.15, R33.1
unnamed: P8.28, R39.2
unnamed: P8.33, R53.2
unnamed: P8.36, R37.2
unnamed: LED1.2 (A), R41.1
unnamed: P8.12, R35.2
unnamed: LED2.1 (C), T6.3 (D)
unnamed: LED2.2 (A), R42.1
unnamed: P9.11, R34.1
unnamed: P8.30, R36.2
unnamed: R38.1, T7.3 (D)
unnamed: P9.12, R40.2
RST/PDN_ADC: R39.1; also elsewhere on the board
SCLK: P9.28; also elsewhere on the board
SENSE_BUTTON: J1.3, P8.34, R54.2
SLCT_LOAD: R33.2; also elsewhere on the board
SWDCLK_BB: P9.42; also elsewhere on the board
SWDCLK_TARGET: P2.13; also elsewhere on the board
SWDIO_BB: P9.41; also elsewhere on the board
SWDIO_TARGET: P2.15; also elsewhere on the board
UART_RX_BB: P9.26; also elsewhere on the board
UART_RX_TARGET: P2.11; also elsewhere on the board
UART_TX_BB: P9.24; also elsewhere on the board
UART_TX_TARGET: P2.9; also elsewhere on the board
VOC_VD: P1.4; also elsewhere on the board
V_BAT: P3.2; also elsewhere on the board
V_BATOK: P2.3; also elsewhere on the board
V_H: D2.1 (C), P1.2; also elsewhere on the board
V_IN_SHT+: P2.4; also elsewhere on the board
V_IN_SHT-: P2.6; also elsewhere on the board
V_SUP_TARGET: P2.1; also elsewhere on the board

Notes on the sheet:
SLCT_LOAD low: External load
Storage capelet headers
User LEDs
Harvesting capelet connector
Target capelet connector
BeagleBone headers
Illuminated button connector


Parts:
C42: 10n; CAPC1005X55
C43, C44: 4.7u; CAPC2012X145
C45: 0.1u; CAPC1005X55
IC13: BQ25504_RGT_16; RGT16_1P7X1P7
L1: 22u; L3225P
ROK1, ROK2: 5.62M; RESC1608X55
ROK3: 1.87M; RESC1608X55
ROV1, ROV2: 5.62M; RESC1608X55
RUV1: 5.62M; RESC1608X55
RUV2: 3.6M; RESC1608X55
S2: ADG736LBRMZRM_10-L; RM_10-L

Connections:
EN_MPPT#: S2.1 (IN1), S2.5 (IN2); also elsewhere on the board
GND: C42.2, C43.2, C44.2, C45.2, IC13.1 (VSS_2), IC13.5 (OT_PROG), IC13.12 (AVSS), IC13.13 (VSS), IC13.17 (EPAD), ROK1.1, ROV1.1, RUV1.1, S2.3 (GND); also elsewhere on the board
unnamed: IC13.16 (LBST), L1.1
VDD: S2.8 (VDD); also elsewhere on the board
VOC_SAMP: IC13.3 (VOC_SAMP), S2.10 (D1)
VOC_VD: S2.9 (S1B); also elsewhere on the board
VREF_SAMP: IC13.4 (VREF_SAMP), S2.6 (D2)
V_BAT: IC13.14 (VBAT); also elsewhere on the board
V_BATOK: IC13.11 (VBAT_OK); also elsewhere on the board
V_BQ: C43.1, IC13.2 (VIN_DC), L1.2; also elsewhere on the board
V_CREF: C42.1, S2.7 (S2B)
V_EMU_V: S2.4 (S2A); also elsewhere on the board
V_OK_HYST: IC13.9 (OK_HYST), ROK2.2, ROK3.1
V_OK_PROG: IC13.10 (OK_PROG), ROK1.2, ROK2.1
V_STR: C44.1, C45.1, IC13.15 (VSTOR), S2.2 (S1A); also elsewhere on the board
V_VBAT_OV: IC13.6 (VBAT_OV), ROV1.2, ROV2.1
V_VBAT_UV: IC13.8 (VBAT_UV), RUV1.2, RUV2.1
V_VRDIV: IC13.7 (VRDIV), ROK3.2, ROV2.2, RUV2.2

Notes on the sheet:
VBAT_OK=2.5V VBAT_OK_HYST=2.92V
VBAT_OV = 3.75V
Analog switch to dynamically switch between built-in MPPT of BQ25504 and reference mode, where it tracks the voltage applied to V_EMU_V
Resistor network for setting overvoltage and 'battery in operating range' voltage thresholds of BQ25505
VBAT_UV = 2.05V


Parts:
C46, C48, C51: 0.1u; CAPC1005X55
C47, C49: 1n; CAPC1005X55
C50: 10n; CAPC1005X55
D3, D4, D5, D6: ACDBQC0130L-HF0402; DIOC1005X55N
IC14: SN74LV4T125PWR; PW0014A_N
IC15: LMP7701MF; DBV5-L
IC16: TXB0304RUTR; RUT0012A
R51: 24; RESC1005X40
R52: 10k; RESC1005X40

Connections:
+3V3: C46.1, C51.1, IC14.14 (VCC), IC16.11 (VCCB); also elsewhere on the board
EN_LVLCNV: IC16.12 (OE); also elsewhere on the board
GND: C46.2, C48.2, C49.2, C50.2, C51.2, IC14.1 (1OE_N), IC14.4 (2OE_N), IC14.7 (GND), IC14.10 (3OE_N), IC14.13 (4OE_N), IC15.2 (V-), IC16.6 (GND); also elsewhere on the board
GPIO0_BB: D5.2 (C); also elsewhere on the board
GPIO0_TARGET: IC14.12 (4A); also elsewhere on the board
GPIO1_BB: D3.2 (C); also elsewhere on the board
GPIO1_TARGET: IC14.5 (2A); also elsewhere on the board
GPIO2_BB: D6.2 (C); also elsewhere on the board
GPIO2_TARGET: IC14.9 (3A); also elsewhere on the board
GPIO3_BB: D4.2 (C); also elsewhere on the board
GPIO3_TARGET: IC14.2 (1A); also elsewhere on the board
unnamed: D4.1 (A), IC14.3 (1Y)
unnamed: C47.1, IC15.1 (OUT), R51.2, R52.1
unnamed: D3.1 (A), IC14.6 (2Y)
unnamed: D6.1 (A), IC14.8 (3Y)
unnamed: D5.1 (A), IC14.11 (4Y)
unnamed: C47.2, IC15.4 (IN-), R52.2
SWDCLK_BB: IC16.9 (B2); also elsewhere on the board
SWDCLK_TARGET: IC16.3 (A2); also elsewhere on the board
SWDIO_BB: IC16.10 (B1); also elsewhere on the board
SWDIO_TARGET: IC16.2 (A1); also elsewhere on the board
UART_RX_BB: IC16.7 (B4); also elsewhere on the board
UART_RX_TARGET: IC16.4 (A3); also elsewhere on the board
UART_TX_BB: IC16.8 (B3); also elsewhere on the board
UART_TX_TARGET: IC16.5 (A4); also elsewhere on the board
VDD: C48.1, IC15.5 (V+); also elsewhere on the board
VDD_TARGET: C50.1, IC16.1 (VCCA), R51.1
V_SUP_TARGET: C49.1, IC15.3 (IN+); also elsewhere on the board

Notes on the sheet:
Bi-directional level converter for UART and SWD signals
Uni-directional, high input impedance level converter for GPIO tracing
Voltage buffer for generating the supply voltage for the bi-directional level converter


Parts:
C26, C28, C52: 1u; CAPC1608X95
C27, C38, C53: 0.1u; CAPC1005X55
C36, C39, C40: 2.2u; CAPC2012X145
C37: 0.47u; CAPC1608X95
C41: 4.7u; CAPC2012X145
IC7: DAC6571IDBVR
IC8: TPS73101DBVR; SOT95P280X145-5N
IC11: CAT24C256WI-GT3; SO08
IC12: LM27762DSSR; VREG_LM27762DSSR
R22, R23, R47, R48, R49: 5.6k; RESC1005X40
R24: 56k; RESC1005X40
R25: 40.2k; RESC1005X40
R26: 30k; RESC1005X40
R43: 300k; RESC1005X40
R44, R46: 100k; RESC1005X40
R45: 294k; RESC1005X40
R50: 10k; RESC1005X40
S4: TMUX1101DCK; DCK5
TP5, TP6: TPSQTP06R; TP06R
WP: TPSQTP06R; TP06R

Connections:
+3V3: C26.1, C27.2, C38.1, IC7.3 (VDD), IC11.8 (VCC), R22.2, R23.2, R47.2, R48.2, R49.2, R50.2; also elsewhere on the board
+5V: C36.1, IC12.3 (VIN); also elsewhere on the board
EN_V_ANLG: IC12.8 (EN_N), IC12.12 (EN_P); also elsewhere on the board
EN_V_FIX: S4.4 (SEL); also elsewhere on the board
GND: C26.2, C27.1, C28.2, C36.2, C38.2, C39.2, C40.2, C41.2, C52.2, C53.2, IC7.2 (GND), IC7.6 (A0), IC8.2 (GND), IC11.1 (A0), IC11.2 (A1), IC11.4 (VSS), IC12.1 (PGOOD), IC12.4 (GND), IC12.13 (EP_GND), R26.2, R44.1, R46.1, S4.3 (GND); also elsewhere on the board
I2C1_SCL: IC7.5 (SCL), R22.1; also elsewhere on the board
I2C1_SDA: IC7.4 (SDA), R23.1; also elsewhere on the board
I2C2_SCL: IC11.6 (SCL), R47.1; also elsewhere on the board
I2C2_SDA: IC11.5 (SDA), R48.1; also elsewhere on the board
unnamed: C52.1, IC8.5 (OUT), R25.1, S4.1 (D)
unnamed: IC8.4 (NR/FB), R24.2, R25.2, R26.1
unnamed: IC12.2 (FB_P), R43.1, R44.2
unnamed: IC7.1 (VOUT), R24.1
unnamed: IC11.7 (WP), R50.1, WP.TP
unnamed: IC12.7 (FB_N), R45.1, R46.2
unnamed: IC11.3 (A2), R49.1
unnamed: C41.1, IC12.5 (CP)
unnamed: C37.2, IC12.9 (C1_N)
unnamed: C37.1, IC12.10 (C1_P)
VDD: C28.1, C40.1, C53.1, IC8.1 (IN), IC8.3 (EN), IC12.11 (OUT_P), R43.2, S4.5 (VDD), TP5.TP; also elsewhere on the board
VSS: C39.1, IC12.6 (OUT_N), R45.2, TP6.TP; also elsewhere on the board
V_LD_SHT+: S4.2 (S); also elsewhere on the board

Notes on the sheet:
Fixed supply voltage for programming/non-harvesting operation of the testbed. The DAC output voltage changes the voltage on the reference pin of the LDO, linearly controlling its output voltage.
Generates the low-noise, positive and negative analog supply voltages
EEPROM for storing BB cape info and calibration data


Board: 4 copper layers, 86.4 x 54.6 mm, 171 parts (0 on the bottom side), 134 nets.

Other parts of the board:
U$1, U$2, U$3: REFMARK

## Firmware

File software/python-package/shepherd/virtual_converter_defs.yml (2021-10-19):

virtconverters:
  # info:
  # - compendium of all parameters & description
  # - base for neutral fallback values if provided yml is sparse
  # - -> it is encouraged to omit redundant parameters
  # TODO: data-source documents if ivcurve was measured and stores window size

  neutral:  # note: can not be used as a valid recorder
    window_size: 250
    voltage_mV: 2500
    voltage_min_mV: 0
    voltage_max_mV: 5000
    current_uA: 0
    setpoint_n: 0.70
    interval_ms: 100
    duration_ms: 0.1
    # underlying recoder
    dynamic_bit: 14 # DAC-bit-resolution - dynamic = smallest step
    wait_cycles: 1 # first cycle: ADC-Sampling & DAC-Writing, further steps: waiting

  cv: # constant voltage
    voltage_mV: 2400

  ci: # constant current (good for recording voc)
    current_uA: 0 # TODO: could be replace by general mppt_po-version with lo

  ivcurve: # triangle-wave (zig zag)
    window_size: 250
    voltage_min_mV: 0
    voltage_max_mV: 5000
    # todo: also add switch for sawtooth as alternative (to triangle-wave)?

  mppt_voc: # open circuit voltage for solar
    setpoint_n: 0.76
    interval_ms: 100     # between measurements
    duration_ms: 0     # of measurement

  mppt_voc_bq: # mppt of TI BQ-Converters for solar
    converter_base: mppt_voc
    setpoint_n: 0.76
    interval_ms: 16000  # between measurements
    duration_ms: 256    # of measurement

  mppt_voc_bqt: # mppt of TI BQ-Converters for thermoelectric
    converter_base: mppt_voc
    setpoint_n: 0.50
    interval_ms: 16000  # between measurements
    duration_ms: 256    # of measurement

  mppt_po: # perturbe & observe
    voltage_min_mV: 0
    voltage_max_mV: 5000
    voltage_step_mV: 20
    interval_ms: 100    # between steps

  mppt_po_opt: # power-optimum in sliding window of iv-curves
    converter_base: mppt_po
    interval_ms: 0

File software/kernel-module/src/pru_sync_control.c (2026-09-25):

#include <linux/delay.h>
#include <linux/hrtimer.h>
#include <linux/io.h> /* gpio0-access */
#include <linux/ktime.h>
#include <linux/math64.h>
#include <linux/slab.h> /* kmalloc */

#include "_shared_mem.h"
#include "_shepherd_config.h"
#include "pru_mem_interface.h"
#include "pru_sync_control.h"

//#define DEBUG_SYNC

#define U32T_MAX (0xFFFFFFFFu)
static uint32_t               sys_ts_over_wrap_ns = U32T_MAX;
static uint64_t               ts_upcoming_ns      = 0;
static uint64_t               ts_previous_ns      = 0; /* for plausibility-check */

static enum hrtimer_restart   trigger_callback(struct hrtimer *timer_for_restart);
static enum hrtimer_restart   sync_callback(struct hrtimer *timer_for_restart);
static enum hrtimer_restart   supervisor_callback(struct hrtimer *timer_for_restart);

/* Timer to trigger fast sync_loop */
static struct hrtimer         trigger_timer;
static struct hrtimer         sync_timer;
static struct hrtimer         supervisor_timer;
static u8                     timers_active = 0u;
static struct SharedMem      *shared_mem    = NULL;

/* debug gpio - gpio0[22] - P8_19 - BUTTON_LED is suitable */
static volatile void __iomem *gpio0set      = NULL;
static volatile void __iomem *gpio0clear    = NULL;
#define GPIO_P819_SET iowrite32(0b1u << 22u, gpio0set);
#define GPIO_P819_CLR iowrite32(0b1u << 22u, gpio0clear);

/* series of halving sleep cycles, sleep less coming slowly near a total of 100ms of sleep */
static const unsigned int TIMER_STEPS_NS[] = {20000000u, 20000000u, 20000000u, 20000000u, 10000000u,
                                              5000000u,  2000000u,  1000000u,  500000u,   200000u,
                                              100000u,   50000u,    20000u};
/* TODO: sleep 100ms - 20 us
* TODO: above halvings sum up to 98870 us */
static const size_t       TIMER_STEPS_NS_SIZE = sizeof(TIMER_STEPS_NS) / sizeof(TIMER_STEPS_NS[0]);
//static unsigned int step_pos = 0;

static uint32_t           info_count          = 6666; /* >6k triggers explanation-message once */
struct sync_data_s        sync_state;
static u8                 init_done       = 0;

/* PI-Tuning
 * - float is hard to use in kernel, so i32 it is ...
 * - Ki already includes 0.1 s sample_interval
 * - values are inverted (inv) and shifted by 10 bit (n10)
 */
const int32_t             kp_inv_n10_init = 1024 / 1.1;
const int32_t             ki_inv_n10_init = 1024 / (0.9 * 0.1); //

void                      sync_exit(void)
{
    timers_active = 0u;

    if (init_done)
    {
        hrtimer_cancel(&trigger_timer);
        hrtimer_cancel(&sync_timer);
        hrtimer_cancel(&supervisor_timer);
    }

    if (gpio0clear != NULL)
    {
        iounmap(gpio0clear);
        gpio0clear = NULL;
    }
    if (gpio0set != NULL)
    {
        iounmap(gpio0set);
        gpio0set = NULL;
    }
    init_done = 0;
    printk(KERN_INFO "shprd.sync: pru-sync-system exited");
}

int sync_init(void)
{
    uint32_t ret_value;

    if (init_done)
    {
        printk(KERN_ERR "shprd.sync: pru-sync-system init requested -> can't init twice!");
        return -1;
    }
    sync_reset();

    gpio0clear = ioremap(0x44E07000u + 0x190u, 4u); // BBB, GPIO0
    if (gpio0clear == NULL)
    {
        printk(KERN_ERR "shprd.k: sync-control mapping of GPIO0CLEAR failed!");
        return -2;
    }
    else
        printk(KERN_INFO "shprd.debug: Gpio0clear @ 0x%X virt, 0x%X phys, %d bytes",
               (uint32_t) gpio0clear, (uint32_t) (0x44E07000u + 0x190u), 4u);

    gpio0set = ioremap(0x44E07000u + 0x194u, 4u);
    if (gpio0set == NULL)
    {
        printk(KERN_ERR "shprd.k: sync-control mapping of GPIO0SET failed!");
        return -3;
    }
    else
        printk(KERN_INFO "shprd.debug: Gpio0set @ 0x%X virt, 0x%X phys, %d bytes",
               (uint32_t) gpio0set, (uint32_t) (0x44E07000u + 0x194u), 4u);

    /* timer for trigger */
    // TODO: HRTIMER_MODE_ABS_HARD wanted, but _HARD not defined in 4.19 (without -RT)
    hrtimer_setup(&trigger_timer, &trigger_callback, CLOCK_REALTIME, HRTIMER_MODE_ABS);

    /* timer for Sync-Loop */
    hrtimer_setup(&sync_timer, &sync_callback, CLOCK_REALTIME, HRTIMER_MODE_ABS);

    init_done = 1;
    printk(KERN_INFO "shprd.sync: pru-sync-system initialized");

    ret_value = hrtimer_is_hres_active(&trigger_timer);
    printk("%sshprd.sync: trigger_hrtimer.hres    = %d (hres wanted)",
           ret_value == 1 ? KERN_INFO : KERN_ERR, ret_value);
    ret_value = trigger_timer.is_rel;
    printk("%sshprd.sync: trigger_hrtimer.is_rel  = %d (abs wanted)",
           ret_value == 0 ? KERN_INFO : KERN_ERR, ret_value);
    ret_value = trigger_timer.is_soft;
    printk("%sshprd.sync: trigger_hrtimer.is_soft = %d (hard wanted)",
           ret_value == 0 ? KERN_INFO : KERN_ERR, ret_value);
    //printk(KERN_INFO "shprd.sync: trigger_hrtimer.is_hard = %d", trigger_timer.is_hard); // needs kernel 5.4+

    /* supervisor checks and corrects next_timestamp of PRU */
    if (pru_shared_mem_io == NULL)
    {
        printk(KERN_ERR "shprd.sync: supervisor needs shared-mem of PRU but got NULL");
        return -4;
    }
    shared_mem = (struct SharedMem *) pru_shared_mem_io;
    hrtimer_setup(&supervisor_timer, &supervisor_callback, CLOCK_REALTIME, HRTIMER_MODE_ABS);

    sync_start();
    return 0;
}

void sync_pause(void)
{
    if (!timers_active)
    {
        printk(KERN_ERR "shprd.sync: pru-sync-system pause requested -> but wasn't running!");
        return;
    }
    timers_active = 0;
    printk(KERN_INFO "shprd.sync: pru-sync-system paused");
}

void sync_start(void)
{
    uint32_t       ns_over_wrap;
    uint64_t       ns_to_next_trigger;
    /* Timestamp system clock */
    const uint64_t ts_now_ns = ktime_get_real_ns();

    if (!init_done)
    {
        printk(KERN_ERR "shprd.sync: pru-sync-system start requested without prior init!");
        return;
    }
    if (timers_active)
    {
        printk(KERN_ERR "shprd.sync: pru-sync-system start requested -> but already running!");
        return;
    }

    sync_reset();

    div_u64_rem(ts_now_ns, SYNC_INTERVAL_NS, &ns_over_wrap);
    if (ns_over_wrap > (SYNC_INTERVAL_NS / 2))
        ns_to_next_trigger = 2 * SYNC_INTERVAL_NS - ns_over_wrap;
    else ns_to_next_trigger = SYNC_INTERVAL_NS - ns_over_wrap; // TODO: unused?

    timers_active = 1;
    hrtimer_start(&sync_timer, ns_to_ktime(ts_now_ns + 1000000u), HRTIMER_MODE_ABS);
    printk(KERN_INFO "shprd.sync: pru-sync-system started");
}

void sync_reset(void)
{
    sync_state.output_sum   = 0;
    sync_state.input_smooth = 20000000;
    sync_state.k_state      = 0;
    sync_state.kp_inv_n10   = kp_inv_n10_init;
    sync_state.ki_inv_n10   = ki_inv_n10_init;
}

static void trigger_start(void)
{
    struct ProtoMsg64 sync_reply64;
    const uint64_t    ts_now_ns = ktime_get_real_ns();

    // initial hard reset of timestamp on PRU on 0.1s-grid
    div_u64_rem(ts_now_ns, SYNC_INTERVAL_NS, &sys_ts_over_wrap_ns);
    ts_upcoming_ns     = ts_now_ns + SYNC_INTERVAL_NS - sys_ts_over_wrap_ns;

    sync_reply64.type  = MSG_SYNC_RESET;
    sync_reply64.value = ts_upcoming_ns;
    pru1_comm_send_sync_reply((struct ProtoMsg *) &sync_reply64);

    while (ktime_get_real_ns() < ts_upcoming_ns - 10000u) udelay(10u);
    mem_interface_trigger(HOST_PRU_EVT_TIMESTAMP);

    ts_previous_ns = 0; // avoids triggering time-jump-detection
    ts_upcoming_ns += SYNC_INTERVAL_NS;
    sys_ts_over_wrap_ns = 0;
    hrtimer_start(&trigger_timer, ns_to_ktime(ts_upcoming_ns),
                  HRTIMER_MODE_ABS); // was: HRTIMER_MODE_ABS_HARD for -rt Kernel

    printk(KERN_INFO "shprd.sync: pru1-init with reset of time to %llu - starting loop",
           ts_upcoming_ns);
}


enum hrtimer_restart trigger_callback(struct hrtimer *timer_for_restart)
{
    uint64_t ns_to_next_trigger;
    uint64_t ts_now_ns;
    // TODO: best would be to get rid of this additional loop - is there a sys-interrupt we can use?
    GPIO_P819_SET;

    /* Raise Interrupt on PRU, telling it to timestamp IEP */
    mem_interface_trigger(HOST_PRU_EVT_TIMESTAMP);

    /* Timestamp system clock */
    ts_now_ns = ktime_get_real_ns();
    GPIO_P819_CLR;

    if (!timers_active) return HRTIMER_NORESTART;
    /*
     * Get distance of system clock from timer wrap.
     * Is negative, when interrupt happened before wrap, positive when after
     */
    div_u64_rem(ts_now_ns, SYNC_INTERVAL_NS, &sys_ts_over_wrap_ns);

    if (sys_ts_over_wrap_ns > (SYNC_INTERVAL_NS / 2))
        ns_to_next_trigger = 2 * SYNC_INTERVAL_NS - sys_ts_over_wrap_ns;
    else ns_to_next_trigger = SYNC_INTERVAL_NS - sys_ts_over_wrap_ns;
    ts_upcoming_ns = ts_now_ns + ns_to_next_trigger;

#ifdef DEBUG_SYNC
    printk(KERN_INFO "shprd.sync: triggered @%llu, next ts = %llu", ts_now_ns, ts_upcoming_ns);
#endif

    // NOTE: without load this trigger is accurate < 4 us
    hrtimer_forward(timer_for_restart, ns_to_ktime(ts_now_ns), ns_to_ktime(ns_to_next_trigger));

    hrtimer_start(&supervisor_timer, ns_to_ktime(ts_upcoming_ns - (SYNC_INTERVAL_NS / 2)),
                  HRTIMER_MODE_ABS);

    return HRTIMER_RESTART;
}

enum hrtimer_restart supervisor_callback(struct hrtimer *timer_for_restart)
{
    /* is executed half way in sync-windows (100 ms) */
    const uint64_t ts_upcoming_pru = shared_mem->next_sync_timestamp_ns;
    if ((ts_upcoming_pru > 0) && (ts_upcoming_pru != ts_upcoming_ns))
    {
        shared_mem->next_sync_timestamp_ns = ts_upcoming_ns;
        printk(KERN_WARNING
               "shprd.sync: upcoming TS of PRU deviates from kMod -> corrected (%lld vs %lld)",
               ts_upcoming_pru, ts_upcoming_ns);
    }

    return HRTIMER_NORESTART;
}
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

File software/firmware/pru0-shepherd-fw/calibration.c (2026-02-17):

#include "calibration.h"
#include "math64_safe.h"
#include "shared_mem.h"
#include <stddef.h>

#define CAL_CFG                                                                                    \
    (*((volatile struct CalibrationConfig *) (PRU_SHARED_MEM_OFFSET +                              \
                                              offsetof(struct SharedMem, calibration_settings))))

void calibration_initialize() {}


/* bring values into adc domain with -> voltage_uV = adc_value * gain_factor + offset
 * original definition in: https://github.com/nes-lab/shepherd/blob/main/docs/user/data_format.rst */
// Note: n8 can overflow uint32, 50mA are 16 bit as uA, 26 bit as nA, 34 bit as nA_n8-factor -> keep multiplication u64
// TODO: negative residue compensation, new undocumented feature to compensate for noise around 0 - current uint-design cuts away negative part and leads to biased mean()
#define NOISE_ESTIMATE_nA   (2000u)
#define RESIDUE_SIZE_FACTOR (30u)
#define RESIDUE_MAX_nA      (NOISE_ESTIMATE_nA * RESIDUE_SIZE_FACTOR)
uint32_t cal_conv_adc_raw_to_nA(const uint32_t current_raw)
{
    const uint32_t I_nA = mul32e(current_raw, CAL_CFG.adc_current_factor_nA_n8) >> 8u;
    // avoid mixing signed and unsigned OPs
    if (CAL_CFG.adc_current_offset_nA >= 0)
    {
        const uint32_t adc_offset_nA = CAL_CFG.adc_current_offset_nA;
        return add32(I_nA, adc_offset_nA);
    }
    else
    {
        static uint32_t negative_residue_nA = 0;
        const uint32_t  adc_offset_nA       = -CAL_CFG.adc_current_offset_nA + negative_residue_nA;

        if (I_nA > adc_offset_nA)
        {
            negative_residue_nA = 0;
            return (I_nA - adc_offset_nA);
        }
        else
        {
            negative_residue_nA = adc_offset_nA - I_nA;
            if (negative_residue_nA > RESIDUE_MAX_nA) negative_residue_nA = RESIDUE_MAX_nA;
            return 0u;
        }
    }
}

/* currently only used by harvester (as emu has no adc for measuring voltage) */
uint32_t cal_conv_adc_raw_to_uV(const uint32_t voltage_raw)
{
    const uint32_t V_uV = mul32(voltage_raw, CAL_CFG.adc_voltage_factor_uV_n8) >> 8u;
    // TODO: wouldn't be mul32e safer?
    // avoid mixing signed and unsigned OPs
    if (CAL_CFG.adc_voltage_offset_uV >= 0)
    {
        const uint32_t adc_offset_uV = CAL_CFG.adc_voltage_offset_uV;
        return add32(V_uV, adc_offset_uV);
    }
    else
    {
        const uint32_t adc_offset_uV = -CAL_CFG.adc_voltage_offset_uV;
        return sub32(V_uV, adc_offset_uV);
    }
}

// safe conversion - 5 V is 13 bit as mV, 23 bit as uV, 31 bit as uV_n8
uint32_t cal_conv_uV_to_dac_raw(const uint32_t voltage_uV)
{
    uint32_t dac_raw;
    // return (((uint64_t)(voltage_uV - CAL_CFG.dac_voltage_offset_uV) * (uint64_t)CAL_CFG.dac_voltage_inv_factor_uV_n20) >> 20u);
    // avoid mixing signed and unsigned OPs
    if (CAL_CFG.dac_voltage_offset_uV >= 0)
    {
        const uint32_t dac_offset_uV = CAL_CFG.dac_voltage_offset_uV;
        if (voltage_uV > dac_offset_uV)
            dac_raw = mul32e(voltage_uV - dac_offset_uV, CAL_CFG.dac_voltage_inv_factor_uV_n20) >>
                      20u;
        else dac_raw = 0u;
    }
    else
    {
        const uint32_t dac_offset_uV = -CAL_CFG.dac_voltage_offset_uV;
        dac_raw = mul32e(voltage_uV + dac_offset_uV, CAL_CFG.dac_voltage_inv_factor_uV_n20) >> 20u;
    }
    return (dac_raw > 0xFFFFu) ? 0xFFFFu : dac_raw;
}

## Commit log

2024-08-06 force current version of core-lib
2024-08-07 harvesting ivcurves: fix max age of samples
2024-09-09 calibration pair - add known units
2024-10-01 ptp-setup - change back to pi-servo
2024-11-29 add voltage-step to HarvesterPRUConfig
2025-03-10 add latest PCB-designfiles
    [Bill of Materials-shepherd_v2_25c.xlsx, Bill of Materials-shepherd_v2_25d.xlsx, Pick Place for shepherd_pcb_v2.5c.csv, Pick Place for shepherd_pcb_v2.5d.csv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]
2025-03-10 move cape v2.5a to deprecated
    [Bill of Materials-shepherd_v2.xlsx, Pick Place for shepherd_pcb_v2.5a.csv, shepherd_pcb_v2.5a_Assembly_Notes.gbr, shepherd_pcb_v2.5a_Bottom_Designator.gbr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]
2025-03-10 move cape v2.5c to deprecated
    [Bill of Materials-shepherd_v2_25c.xlsx, Pick Place for shepherd_pcb_v2.5c.csv, shepherd_pcb_v2.5c_Assembly_Notes.gbr, shepherd_pcb_v2.5c_Bottom_Designator.gbr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]
2025-03-10 update documentation
    [beaglebone_pinout_concept.xlsx]
2025-03-10 more documentation
    [beaglebone_pinout_concept.xlsx]
2025-03-10 remove files
    [Emulator.SchDoc, Host-Interface.SchDoc, LevelTranslators.SchDoc, Misc.SchDoc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]
2025-03-31 update cape doc
    [Bill of Materials-shepherd_v2_25d_pnp.xlsx]
2025-04-02 add new hardware revision
    [Bill of Materials-shepherd_v2.xlsx, Pick Place for shepherd_pcb_v2.5e.csv, shepherd_pcb_v2.5e_Assembly_Notes.gbr, shepherd_pcb_v2.5e_Bottom_Designator.gbr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]
2025-04-02 move old hw to deprecated
    [Bill of Materials-shepherd_v2_25d.xlsx, Bill of Materials-shepherd_v2_25d_pnp.xlsx, Pick Place for shepherd_pcb_v2.5d.csv, Pick Place for shepherd_pcb_v2.5d_pa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]
2025-04-02 deprecate power board
    [Bill of Materials-shepherd_power.xlsx, Pick Place for board.csv, board_Assembly_Notes.gbr, board_Bottom_Designator.gbr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]
2025-04-21 add battery model to PRU
2025-04-21 hacky integration of battery to get performance numbers
2025-04-30 remove threaded access to shared mem
2025-05-21 established `ivsurface` and `ivtrace` instead of curves and sample
2025-06-16 herd - allow quiet run_task() & sort output that gets printed
2025-06-18 add power-recorder
2025-06-18 add custom samplerate and only-power option to writer
2025-06-18 activate new power-tracing options in emu & hrv
2025-06-18 small bugfix for not available power-tracing
2025-06-25 herd - give threads a configurable timeout
2025-06-26 herd - try more response thread-monitor in .run_cmd()
2025-06-26 herd - bring new thread-monitor to .get_file() & .put_file()
2025-06-28 sheep - make power-recorder float64 safe
2025-09-15 add doc for virtual battery
2025-09-22 add doc for battery storage
2025-09-22 migrate battery-model to revised virtual storage
2025-11-14 pru0 - improve control-flow
2025-12-05 nfs-mounting optimized
2026-01-30 use correct scaling for sampling intermediate power values
2026-02-11 optimize LUT-division of PRU for new battery model
2026-02-18 rename legacy device tree file
2026-02-18 copy device tree
2026-02-18 add device-tree for cape hw ver 2.5
2026-02-18 rename BATOK to power_good and increase size (bool to u8)
2026-02-18 extend power-good-algorithm to generate two signals
2026-02-23 PRU0 - add error when gpio-trace result won't fit into current buffer-design
2026-02-23 PRU0 - disable LED-DEBUGGING as all available pins are used for IO on cape 2.5 (will also make GPIO-Tracing faster)
2026-03-06 build both device trees
2026-03-21 add case for observers
    [Part Studio 1 - CaseBack.step, Part Studio 1 - CaseMain.step]
2026-03-21 deprecate old lasercut case
2026-03-23 add cage for cape
    [cape_cage_PLA_x6.3mf, cape_v25_cage.scad, cape_v25_cage.stl, misc_parts.scad]
2026-03-23 add bulk holders for PCBs
    [shepherd-cape-bulk-holder.scad, shepherd-cape-bulk-holder.stl, shepherd-target-bulk-holder.3mf, shepherd-target-bulk-holder.scad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]
2026-03-23 add cable clip
    [NW CableClip.step]
2026-04-07 revert deprecation of cape 2.4c, as it is essential for harvesting
    [Bill of Materials-shepherd_v2.4.xlsx, Pick Place for shepherd_pcb_v2.4.csv, shepherd_pcb_v2.4_Assembly_Notes.gbr, shepherd_pcb_v2.4_Copper_Signal_1.gbr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]
2026-04-29 sheep - prevent early exit if power-tracing is disabled
2026-04-29 sheep - transform pru_util into a monitor-thread
2026-04-30 revert Monitor for pru-util (multi-threading issue while accessing mem)
2026-06-18 Device-tree - add memory reserve for later kernels
2026-06-25 bring in changes from riotee-sbw-device
